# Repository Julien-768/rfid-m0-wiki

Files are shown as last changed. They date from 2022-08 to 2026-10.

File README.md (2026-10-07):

# RFID-M0 Documentation

Documentation for the **RFID-M0** autonomous monitoring device developed by the MIBE technical platform at IPHC.

This repository contains the source files used to build the RFID-M0 documentation website.

## Repository

The **GitLab repository is the primary project repository**. The GitHub repository is maintained as a mirror.

- **GitLab:** <https://gitlab.in2p3.fr/rfid-m0/rfid.m0.wiki>
- **GitHub:** <https://github.com/Julien-768/rfid-m0-wiki>

## Documentation website

The latest version of the documentation is available online:

**<https://rfid-m0.pages.in2p3.fr/rfid.m0.wiki/latest/>**

## Contents

The documentation covers the complete RFID-M0 project, including:

- device operation;
- user procedures;
- configuration;
- hardware architecture;
- electronic boards;
- power supply;
- RFID antennas;
- assembly;
- programming;
- manufacturing;
- testing and maintenance;
- advanced technical topics.

The documentation is available in **English and French**.

## Repository structure

```text
rfid.m0.wiki/
├── docs/               # Documentation source files
├── overrides/          # MkDocs theme customizations
├── mkdocs.yml          # MkDocs configuration
├── requirements.txt    # Python dependencies
├── pyproject.toml      # Project/tool configuration
├── .markdownlint.json  # Markdown linting configuration
└── .prettierrc         # Prettier configuration
```

## Requirements

The documentation is built using **MkDocs** with the **Material for MkDocs** theme.

Install the required Python packages with:

```bash
pip install -r requirements.txt
```

## Local development

To preview the documentation locally:

```bash
mkdocs serve
```

The development server is then available at:

```text
http://127.0.0.1:8000/
```

To build the static website:

```bash
mkdocs build
```

The generated website is placed in the `site/` directory.

## Firmware

The RFID-M0 firmware is maintained in a separate repository.

- **GitLab:** <https://gitlab.in2p3.fr/rfid-m0/rfid.m0.code>
- **GitHub:** <https://github.com/Julien-768/rfid-m0-code>

Firmware changes that affect device operation or documented behaviour should be reflected in this repository.

## Contributing

Documentation improvements, corrections, and clarifications are welcome.

When modifying documentation, please keep the structure and terminology consistent with the existing project documentation.

## License

This documentation is distributed under the **GNU General Public License v3.0**.

See [`LICENSE.txt`](LICENSE.txt) for the complete license text.

## Project

**RFID-M0**
MIBE Technical Platform — IPHC

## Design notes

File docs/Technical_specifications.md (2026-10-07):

# Technical specifications

## Memory

The system stores its data on a Micro-SD card.

- The maximal supported size is 32GB ([SD and SDHC](https://www.arduino.cc/reference/en/libraries/sd/) card supported).
- For example, a 2GB SD card can record ~5,100,000,000 detections with tags (**~59 continuous days** with one detection per second).

## Powering

Several powering options are proposed :

- Lithium powered
  - 3.6V 20Ah 72Wh Li-ion battery (Weight ~0.3kg - Cost ~80€ )
  - 3.6V 20Ah 72Wh Li-ion battery (Weight ~0.3kg - Cost ~80€ ) + a solar panel

- Lead powered
  - 12V 5.4Ah 64.8Wh Lead battery (Weight ~1.7kg - Cost ~40€ ), for rodent device

## Consumption & Autonomy

For details about components consumption and autonomy calculation, refers to the [calculation sheet](./assets/images/User_description/Consumption_and_autonomy.xlsx).

### Autonomy

The autonomy varies according to the software configuration. Here is the autonomy measured with a 65 Wh battery

| System configuration                |  Autonomy  | Equivalent consumption [W.h] | Equivalent consumption per day |
| ----------------------------------- | :--------: | :--------------------------: | :----------------------------: |
| IR On - RFID (On) (1) - 12/24h mode | 17d 7h 9m  |           0.16 W.h           |            3.8 /day            |
| IR On - RFID (On) (1) - 24/24h mode | 10d 22h 9m |           0.25 W.h           |            6 W/day             |
| IR Off - RFID On - 12/24h mode      | 9d 8h 37m  |           0.29 W.h           |            7 W/day             |
| IR Off - RFID On - 24/24h mode      | 5d 6h 34m  |           0.52 W.h           |           12.5 W/day           |

??? note "RFID (On)"

      RFID triggered by infrared sensors

??? note Assomptions made for autonomy estimation

    - 50 detections with RFID tag per hour
    - One detection = 5 seconds in front of sensor, including 1 second to read the RFID tag
    - a 64.8Wh 12V 5.4 A.h Lead battery (more pessimistic situation)
    - T = 20°c

Some notions have to be kept in mind :

- There is no consumption difference if one or two IR sensors are active. In both cases, the two emitters & receivers are powered
- If the two IR sensors are inactive, the RFID is always in research mode (IR Off - RFID On) except during sleep mode
- If the temperature sensor is active, the IR receiver modules are powered even if opt_IR_1 & opt_IR_2 are False (same power supply)
- During sleep mode, only the microcontroler and the Real Time Clock are powered

### Component consumption

| Board           | Component                    |   Mode   | Power consumption [mW] |
| --------------- | ---------------------------- | :------: | :--------------------: |
| Power board 5V  | Power board                  |    -     |           43           |
| Power board 12V | Power board                  |    -     |          112           |
| Main board      | Feather (including SD) + RTC |    -     |           65           |
| Main board      | RFID reader & antenna        | Standby  |           80           |
| Main board      | RFID reader & antenna        | Research |          450           |
| Main board      | RFID reader & antenna        | Reading  |          232           |
| Main board      | 1 IR Emitting Diode          |    -     |          15.8          |
| Main board      | 1 IR receiver module         |    -     |          1.3           |
| Main board      | + 3.3V regulator             |    -     |           45           |

The consumptions are measured for T = 20°c.

The IR Emitting Diode is considered with 220 Ohm resistor and 50% PWM duty cycle.

**Be careful to the SD card consumption** : Its consumption can vary from 1 et 10mA according to the manufacturer and the production batch.

### Rodent device dimensions

The system is designed to be integrated into a [1150 hard case Pelicase](https://www.peli.com/eu/fr/product/cases/protector/1150) (240 x 198 x 109 mm).

<a href="../assets/images/User_description/1150_pelicase.jpg">
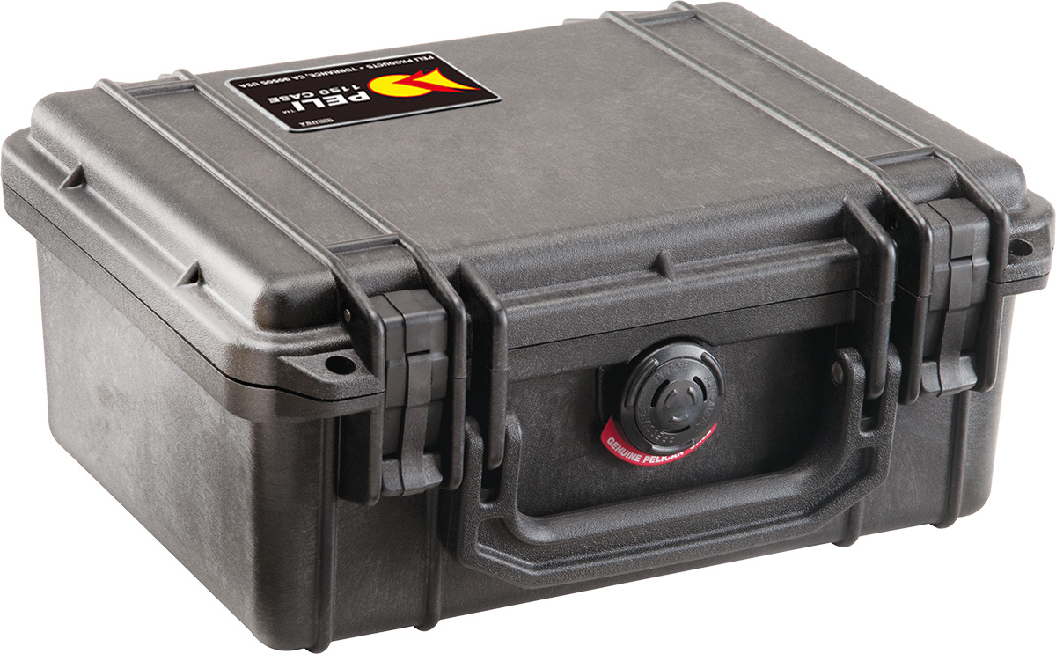
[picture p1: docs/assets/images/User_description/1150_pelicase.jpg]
1150 Pelicase

</a>

The operating tempererature range is 0°c to 50°c.

<!-- | System configuration                | Consumption [W.h] |  Autonomy  |
| ----------------------------------- | :---------------: | :--------: |
| I---------------------------------e | 3---------------7 | 1--------m |
| IR On - RFID (On) (1) - 24/24h mode | 5.9               | 10d 22h 9m |
| IR Off - RFID On - 12/24h mode      | 6.9               | 9d 8h 37m  |
| IR Off - RFID On - 24/24h mode      | 12.3              | 5d 6h 34m  | -->

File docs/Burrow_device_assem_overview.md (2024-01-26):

# Assembly a burrow device

This section describes the different steps to follow to assemble a device that monitor a burrow occupation. The list of required material is avaible at this [link](https://gitlab.in2p3.fr/rfid.m0/rfid.m0.elec/-/raw/master/BOM_append.xlsx?inline=false).

Firstly, a **burrow antenna is build**. This antenna receives the RFID antenna, able to detect RFID tags, but also two infrared sensors. The manufacturing of this device is based on 3D-printed parts in which electronic components are inserted. Resin is then added to protect the components from environment and rodents.

<a href="../assets/images/Antennas/burrow_antenna.jpg">
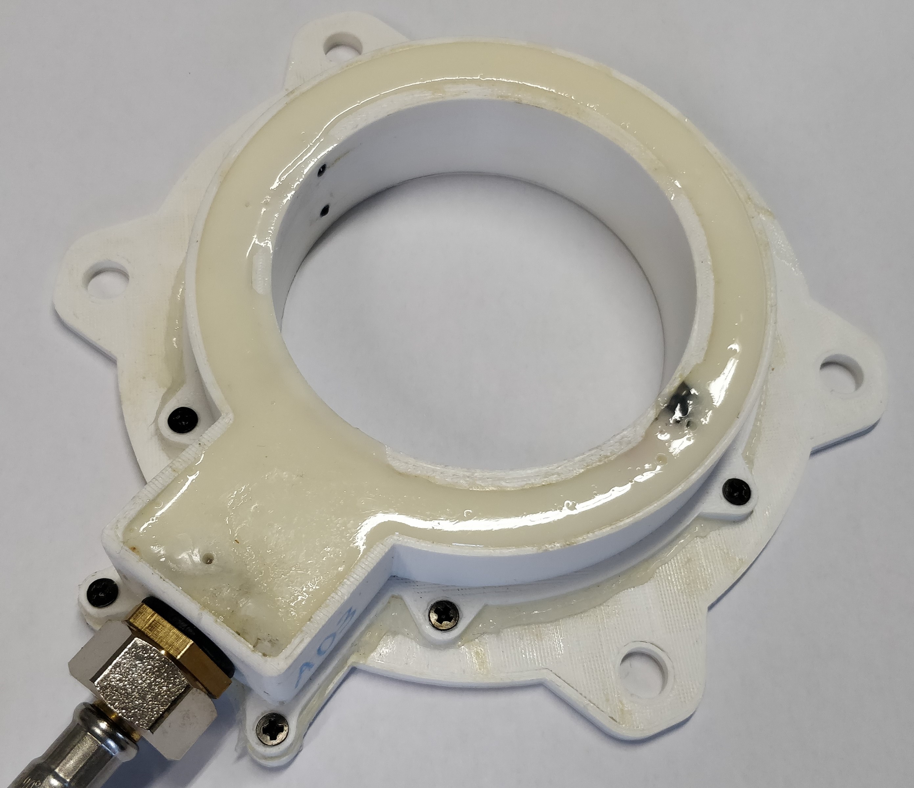
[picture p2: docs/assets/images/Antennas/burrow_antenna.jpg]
snapshot of the burrow antenna in the lab

</a>

Secondly **electronic component are mounted** into the boards. There are three boards that are required :

- A main board
- A power board in charge of power management
- A RFID reader based on a Tectus board

The last board only requires to weld some connectors. The power board (two variants exist) must be chosen according to the battery technology.

**A case is then prepared** and assembled with the antenna. The machining of the case must be carefully done to prevent water from entering the housing.

<a href="../assets/images/Case/Case_with_components.jpg">
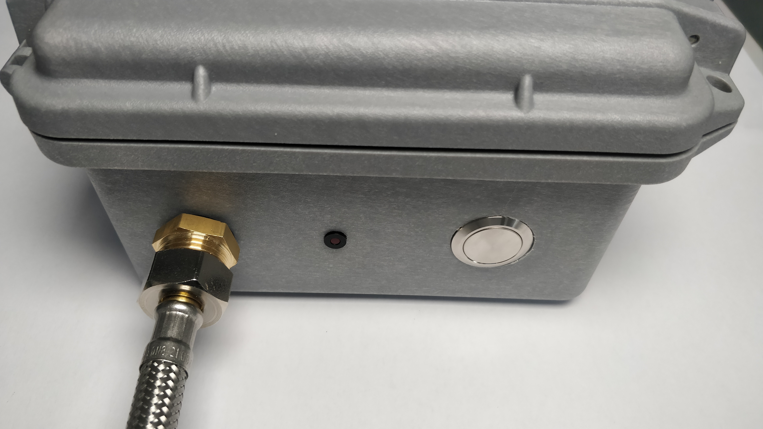
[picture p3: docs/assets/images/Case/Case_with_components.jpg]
Case with external components

</a>

The last step before the final assembling is to **program the main board**. This step must be done after the electronic assembling in order to correctly set the time of the real-time-clock (CR1220 coin cell must be inserted).

Finally **all the components are installed into the case**. This step requires wiring to connect the different boards together.

Once battery inserted and connected, the device will be ready for [checking](Check_burrow_device.md).

<a href="../assets/images/Burrow_assembling/Final_assembling.jpg">
Final assembling
</a>

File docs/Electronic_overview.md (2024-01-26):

# Overview

The electronic of the device is composed of several boards :

- A main board that receive most of the component and is linked to the sensors
- A power board in charge to manage the energy of the system and deliver a regulated 5v
- A RFID board that, once associated to an antenna, reads the RFID tags
- An optional multiplex board to connect two antennas to the main board

## Schematic of the system

<a href="../assets/images/Manufacturing/General_schematic.svg">
General schematic
</a>

For multiplexed version, [refer here](./assets/images/Manufacturing/General_schematic_multiplex.svg)

## Main board

The main board performs most of the system's functions :

- Sensor reading
- Data recording
- Time / Date management
- Security management (temperature and battery monitoring)

This board is **3.3V-logic level and powered in 5V** by one associated power board.

## Power board

The power board ensures the power and battery management to create a 5V.
Some components are plugged into it :

- The SWITCH button that **connect / disconnect the battery** to the power board
- The START button that permits the user to **safely switch On / Off** the system
- An optional solar panel to reload the battery

A 3-wire cable connect the main board to the power board :

- EN : This line permits the main board to pilot the power supply (self-hold function)
- SW : This line allow the main board to read the START button status (pressed / released)
- VBAT : Battery voltage compatible with 3.3V-logic level

To be compatible with different battery technologies, two power boards are available :

- [5V power supply board](./Power-5V.md) to use Li-Po or Li-Ion battery. A reload by USB-C or an optional solar panel is also possible.
- [12V power supply board](./Power-12V.md) to use lead-battery from 9V to 18V.

## Multiplex board

The multiplex board ensures to connect two antennas to the main board by routing :

- RFID signal
- Infrared signal
- Power signal

This board is **powered in 5V** and is compatible with **3.3V or 5V-logic level**.

Note : If a multiplex board is used, the servo motor cannot be connected (same pin)

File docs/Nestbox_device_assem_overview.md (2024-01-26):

# Assembly a nest box device

This section describes the different steps to follow to assemble a device that monitor a nest box occupation. The list of required material is avaible at this [BOM link](https://gitlab.in2p3.fr/rfid.m0/rfid.m0.elec/-/raw/master/BOM_append.xlsx?inline=false).

Firstly, a **nest box antenna is build**. This antenna receives the RFID antenna, able to detect RFID tags, but also two infrared sensors. The manufacturing of this device is based on 3D-printed parts in which electronic components are inserted and glued.

<a href="../assets/images/Antennas/schwegler_antenna.jpg">
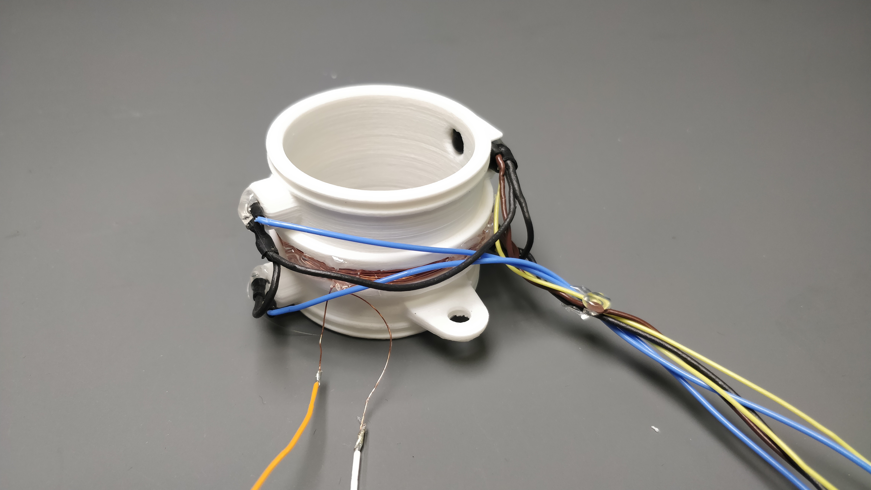
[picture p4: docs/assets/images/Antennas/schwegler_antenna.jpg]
wired antenna and infrared beams around the 3D print in the lab

</a>

Secondly **electronic component are mounted** into the boards. There are three boards that are required :

- A main board
- A power board in charge of power management
- A RFID reader based on a Tectus board

The RFID board only requires to weld some connectors.

Due to the dimensions of the nest box, **only the 5v power board can be used**. In addition, the compatibility with an additional solar panel or USB charger is possible.

The last step before the final assembling is to **program the main board**. This step must be done after the electronic assembling in order to correctly set the time of the real-time-clock (CR1220 coin cell must be inserted).

Finally **all the components are installed into the nest box and wired**. This step requires 3D-printing and wiring to connect the different boards together.

Once battery inserted and connected, the device will be ready.

<a href="../assets/images/Nest_box_assem/Nest_box_closed.jpg">
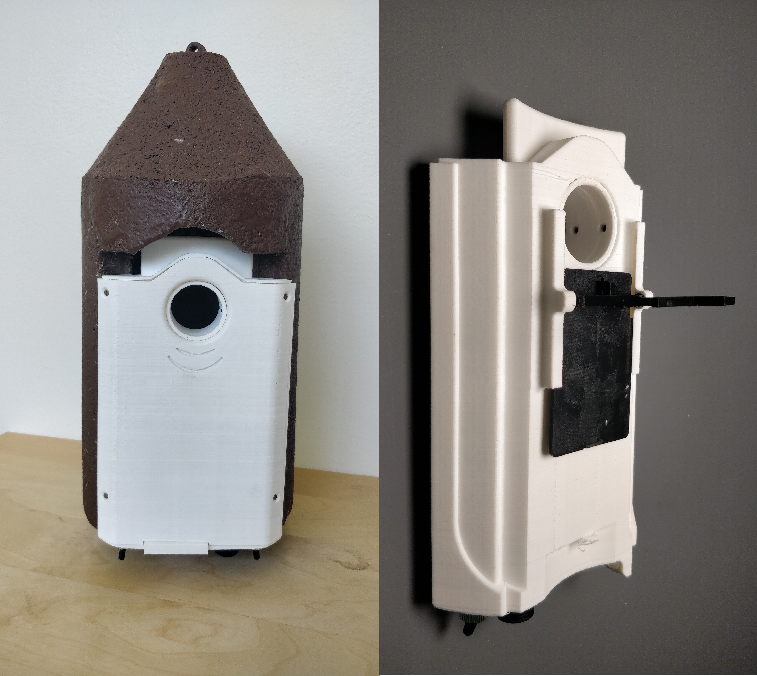
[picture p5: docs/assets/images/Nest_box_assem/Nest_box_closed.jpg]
Nest box assembled

</a>

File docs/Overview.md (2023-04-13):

# Overview

L'alimentation de la carte Acquisition est en 5V.

La "carte Power" assure la conversion et la gestion de la batterie, pour envoyer en sortie du 5V.

- L'interrupteur général coupe l'alimentation en entrée du convertisseur VBAT / 5V.
- Le bouton marche arrêt ou Switch, permet par un appui prolongé, l'allumage ou l'éteignage du système par le software.
- La recharge par panneau solaire est optionnel.

Les 3 câbles de données [EN;SW;Vbat] entre les 2 cartes servent à :

- EN: si cette entrée est mise à l'état haut, l'alimentation de l'acquisition est coupée.
- SW: passe à l'état haut si le bouton marche/arrêt est appuyé.
- Vbat: renvoie l'information de la tension de la batterie entre 0 et 3.3V à l'aide d'un pont diviseur

TODO Power_schematic_géné "/uploads/53b2525b21db5eaeaf2a90db03fd7f05/Power_schematic_géné.png"

Il a été conçu 2 types de carte Power:

- [5V power supply board](./Power-5V.md) qui permet d'utiliser des batteries Li-Po ou Li-Ion avec l'option rechargement par panneau solaire ou par USB C.
- [12V power supply board](./Power-12V.md) qui permet d'utiliser des batteries allant de 9V à 18V.

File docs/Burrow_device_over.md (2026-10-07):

# Device description

The purpose of this system is to monitor certain individuals.
A circular antenna, equipped with sensors and placed at the entrance of a burrow, can detect the passage of individuals and read their RFID tags (if existing).
All this data is collected on an memory card with timestamp.

The entire system is contained in a case for easy transport and installation.

<a href="../assets/images/User_description/Complete_system.jpg">
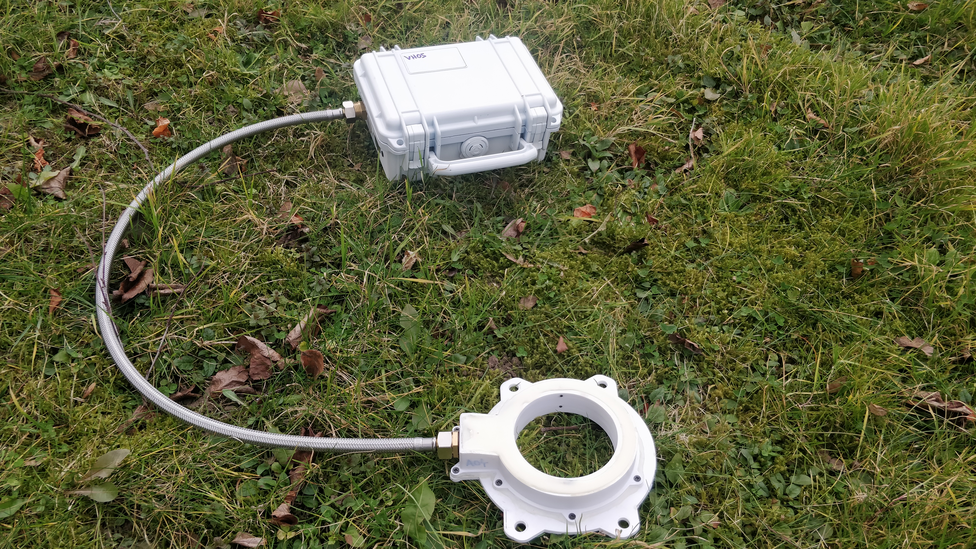
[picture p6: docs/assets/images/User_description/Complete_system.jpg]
Complete system

</a>
<<<<<<< Updated upstream

## System constitution

=======

> > > > > > > Stashed changes

The system consists of a terrier antenna and a case.
The antenna incorporates two infrared transmitters / receivers as well as an RFID antenna.

<a href="../assets/images/User_description/Burrow_device_detailed.jpg">
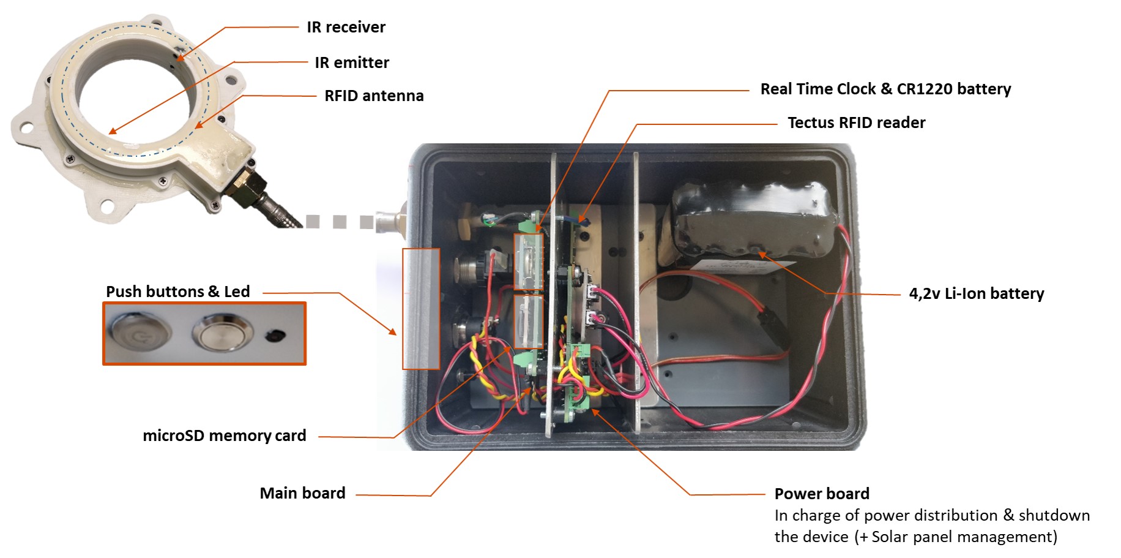
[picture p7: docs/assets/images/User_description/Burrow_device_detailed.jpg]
Burrow device detailed

</a>

Note : IR sensor noted "IR 1" in the record file is the one mounted on the top of the antenna (small diameter side)

<a href="../assets/images/User_description/IR_sensor_arrangement.png">
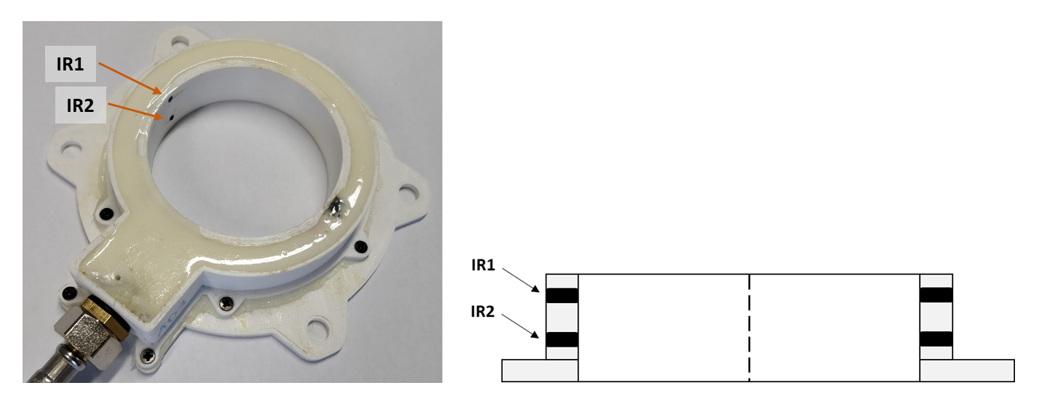
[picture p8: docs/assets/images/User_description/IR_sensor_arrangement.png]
IR sensors arrangement

</a>

The case contains all the embedded electronics, the battery, the clock, the micro-SD memory card and the start-up buttons.
On the outside of the case you'll find:

- A main switch button : Used to connect / disconnect the system with the battery
- A switch button : Used to power-on / power-off the system / get the battery status
- A red LED : Used by the system to interact with the user

<a href="../assets/images/Procedure/External_component.png">
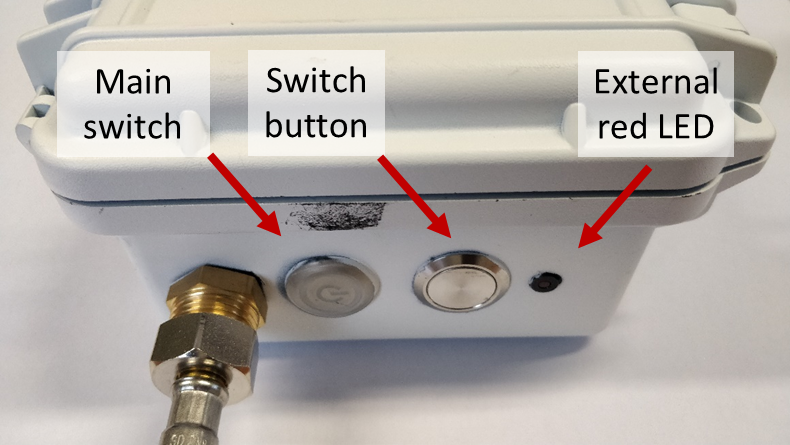
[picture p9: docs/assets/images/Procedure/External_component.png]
External component

</a>

Inside the case is:

- A battery (4.2V Li-ion or 12V Lead version)
- A slot for the micro-SD memory card
- A CR1220 3V battery for the Real-Time Clock

<a href="../assets/images/User_description/Internal_component.png">
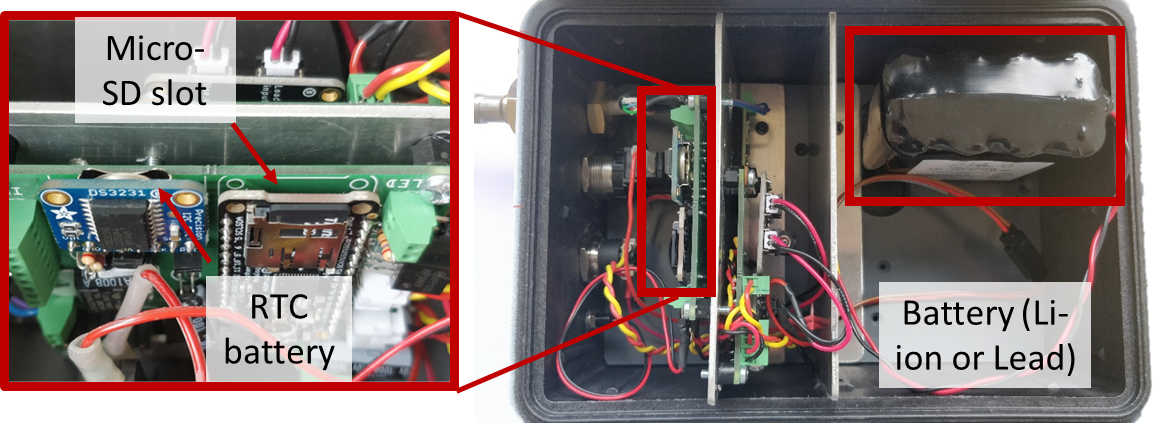
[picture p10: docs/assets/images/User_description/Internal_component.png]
Internal component

</a>

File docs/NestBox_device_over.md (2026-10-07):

# Device description

The purpose of this system is to monitor certain birds. The entrance of a nest box is equipped with sensors to detect the passage of individuals and read their RFID tags (if existing). All this data is collected on a memory card with a timestamp.

Optionally, the nest box door can be closed to capture targeted individuals: None, All, specific RFID tag, or untagged.

The entire system is contained in a door compatible with [Schwegler nest box 2M](https://www.schwegler-natur.de/portfolio_1408366639/nisthoehle-2m/?lang=en).

<a href="../assets/images/User_description/Nest_box_installed.jpg">
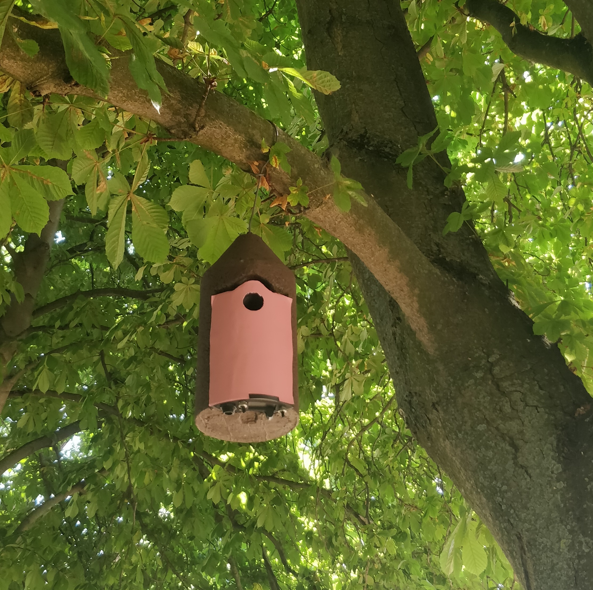
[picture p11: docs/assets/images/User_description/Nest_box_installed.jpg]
Nest box installed

</a>

## Mechanical specifications

### Dimensions

The manufactured door is approximately 210 mm high, 122 mm wide, and 34 mm deep.

### 3D preview

<iframe id="vs_iframe" src="https://www.viewstl.com/?embedded&url=https%3A%2F%2Fgitlab.in2p3.fr%2Frfid.m0%2Frfid.m0.meca%2F-%2Fraw%2Fmaster%2Fantenna_schwegler%2F3D_print%2FFake_device%2FAssembly.stl%3Finline%3Dfalse&orientation=bottom&shading=flat&bgcolor=transparent" style="border:0;margin:0;width:100%;height:601px;"></iframe>

## System Components and Features

### 1 - Entrance Components

The entrance of the nest box incorporates two infrared transmitters/receivers as well as an RFID antenna.

**Note:** The IR sensor noted as "IR 1" in the record file is the one mounted at the entrance (exterior side).

### 2 - Bottom Components

The bottom of the nest box allows the user to interact with the system and its battery:

- A main switch button: Used to connect/disconnect the system from the battery.
- A switch button: Used to power on/power off the system or get the battery status.
- A red LED: Used by the system to interact with the user.
- A mini-USB port: Used to recharge the internal battery or connect an additional battery to extend autonomy (power bank, solar panel, etc.).
- A ring: Used to hold a power bank via a carabiner.

<a href="../assets/images/User_description/Nest_box_Ext_comp.jpg">
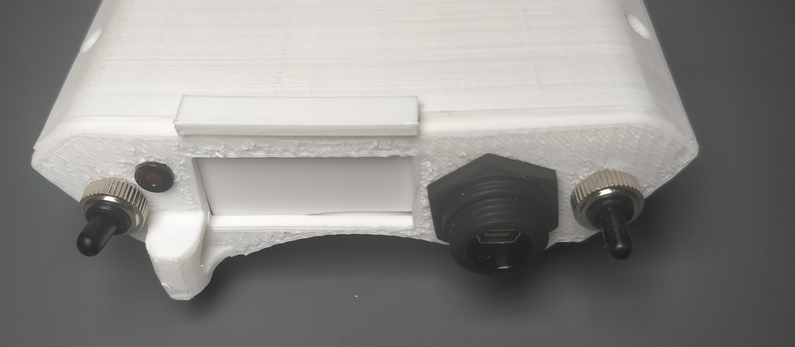
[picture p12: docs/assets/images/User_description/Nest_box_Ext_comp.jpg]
Nest box external component

</a>

### 3 - Technical Door

By sliding the technical door, it is possible to access:

- A slot for the micro-SD memory card.
- A CR1220 3V battery for the Real-Time Clock.

<a href="../assets/images/User_description/Nest_box_Int_comp.jpg">
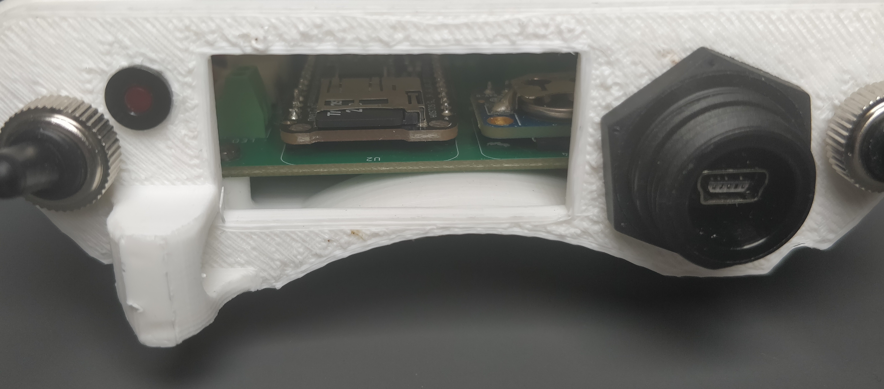
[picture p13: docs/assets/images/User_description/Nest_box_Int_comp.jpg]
Nest box internal component

</a>

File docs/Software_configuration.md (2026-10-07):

# Software configuration

The device configuration is split into two files:

- `hw_assem.cfg`: hardware and device identification parameters.
- `config.cfg`: functional and operating parameters.

These files allow the device to be adapted to the specific hardware and application requirements.

## Hardware configuration — `hw_assem.cfg`

The `hw_assem.cfg` file contains hardware identification and device specification parameters.

| Parameter name      | Description                                                                             | Default / example     |
| ------------------- | --------------------------------------------------------------------------------------- | --------------------- |
| `uid_mainboard`     | Unique identifier of the mainboard (FeatherM0), automatically retrieved by the software | Device-specific       |
| `uid_light_sensor1` | Unique identifier of light sensor 1, automatically retrieved by the software            | Installation-specific |
| `uid_light_sensor2` | Unique identifier of light sensor 2, automatically retrieved by the software            | Installation-specific |
| `uid_software`      | Unique software identifier used to identify the specific firmware version installed     | Installation-specific |
| `uid_experiment`    | Unique identifier of the experiment or project                                          | Installation-specific |
| `device_sn`         | Device serial number used to uniquely identify the physical unit                        | Empty                 |
| `battery_type`      | Type of battery used by the device                                                      | `liion_1s`            |
| `rtc_type`          | Real-Time Clock module used by the device                                               | `ds3231`              |

The `uid_light_sensor1`, `uid_light_sensor2`, `uid_software`, `uid_experiment` and `device_sn` parameters are specific to each installation and should be configured according to the deployed device.

## Functional configuration — `config.cfg`

The `config.cfg` file contains the parameters controlling the functional behavior of the device.

| Parameter name           | Description                                                                               | Values / default          |
| ------------------------ | ----------------------------------------------------------------------------------------- | ------------------------- |
| `use_buffer`             | Enables or disables the use of a temporary data buffer before writing data to the SD card | `{true, false}` — `false` |
| `enable_ir1`             | Enables or disables infrared sensor 1                                                     | `{true, false}` — `true`  |
| `enable_ir2`             | Enables or disables infrared sensor 2                                                     | `{true, false}` — `true`  |
| `enable_rfid`            | Enables or disables the RFID reader                                                       | `{true, false}` — `true`  |
| `rfid_mode`              | Defines how and when the RFID reader is activated                                         | `{0, 1, 2}` — `1`         |
| `enable_vbat`            | Enables or disables battery voltage measurement                                           | `{true, false}` — `true`  |
| `acquisition_interval_s` | Interval between two consecutive data acquisitions, in seconds                            | `[1..xx]` — `60`          |
| `schedule_start_hour`    | Operating schedule start hour                                                             | `[0..23]` — `10`          |
| `schedule_start_minute`  | Operating schedule start minute                                                           | `[0..59]` — `00`          |
| `schedule_end_hour`      | Operating schedule end hour                                                               | `[0..23]` — `18`          |
| `schedule_end_minute`    | Operating schedule end minute                                                             | `[0..59]` — `30`          |

The `schedule_start_*` and `schedule_end_*` parameters define the automatic operating period of the device. With the default values shown above, the operating period is **10:00 to 18:30**.

## RFID mode

The `rfid_mode` parameter defines how and when the RFID reader is activated.

| Value | Mode        | Behavior                                                                                                                                                                                                           | Power consumption |
| ----: | ----------- | ------------------------------------------------------------------------------------------------------------------------------------------------------------------------------------------------------------------ | ----------------- |
|   `0` | Disabled    | The RFID reader is switched off. No tag detection is performed.                                                                                                                                                    | Very low          |
|   `1` | Continuous  | The RFID reader remains continuously active and detects tags continuously.                                                                                                                                         | High              |
|   `2` | On IR event | The RFID reader is activated temporarily following a detection by an infrared sensor.This mode is suitable for relatively large or slow-moving animals that take sufficient time to pass through the RFID antenna. | Moderate          |

### Mode 0 — Disabled

The RFID reader is switched off and no RFID tag detection is performed.

This mode can be used when RFID functionality is not required.

### Mode 1 — Continuous

The RFID reader remains continuously active and can detect tags at any time.

This mode provides continuous RFID availability but results in higher power consumption.

### Mode 2 — On IR event

The RFID reader is activated temporarily following an event detected by an infrared sensor.

This mode reduces power consumption by activating the RFID reader only when an IR event occurs.

**Note:** Mode `2` requires at least one infrared sensor to be enabled (`enable_ir1` or `enable_ir2`).

## RFID activation timing

In mode `2`, the RFID reader is activated for a limited period following an IR event.

The default activation period is between **2 and 5 seconds**. A **1-second debounce period** is used to avoid repeated detections of the same tag.

These timings are predefined and do not need to be modified through the configuration file.

## Editing the configuration files

To modify a configuration file:

1. Remove the SD card from the device and insert it into a computer.
2. Locate the required configuration file (`hw_assem.cfg` or `config.cfg`).
3. Open the file with a text editor.
4. Modify the required parameters.
5. Save the file and reinsert the SD card into the device.

_NOTE:_ Take care to preserve the file syntax when modifying configuration parameters. Incorrect formatting or invalid values may prevent the device from loading the configuration correctly.

If a required configuration file is not present on the SD card, the device can automatically create it with its default values.

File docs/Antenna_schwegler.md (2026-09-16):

# Antenna for Schwegler

This antenna is designed for use on 3D printed door for [Schwegler nest box 2M](https://www.schwegler-natur.de/portfolio_1408366639/nisthoehle-2m/?lang=en), it is suitable with the Tectus RFID reader TITAN 4004 (also know as TLB-30-USB).

<a href="../assets/images/Antennas/schwegler_antenna.jpg">
<<<<<<< Updated upstream
wired antenna and infrared beams around the 3D print in the lab
=======
wired antenna and infrared beams around the 3D print in the lab
>>>>>>> Stashed changes
</a>

## Radiating pattern

The radiation pattern was measured with a 2.3mm EM4102 PIT Bird Tag from [Eccel Technology Ltd.](https://eccel.co.uk/product/2-3mm-em4102-pit-bird-tag-black/)
The read range is 400 mm (typical values) with a EM4102 transponders (1.7 mm Ø) in the best conditions.
The following results are measured on an antenna with a quality factor Q = 23.

<a href="../assets/images/Antennas/schwegler_radiation_best.png">
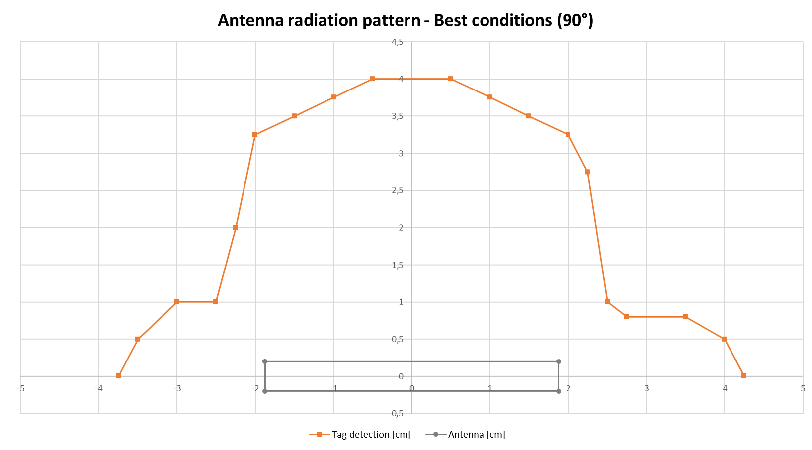
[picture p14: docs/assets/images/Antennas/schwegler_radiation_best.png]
image of the radiation pattern of the Schwegler antenna with best TAG orientation

</a>
<a href="../assets/images/Antennas/schwegler_radiation_worst.png">
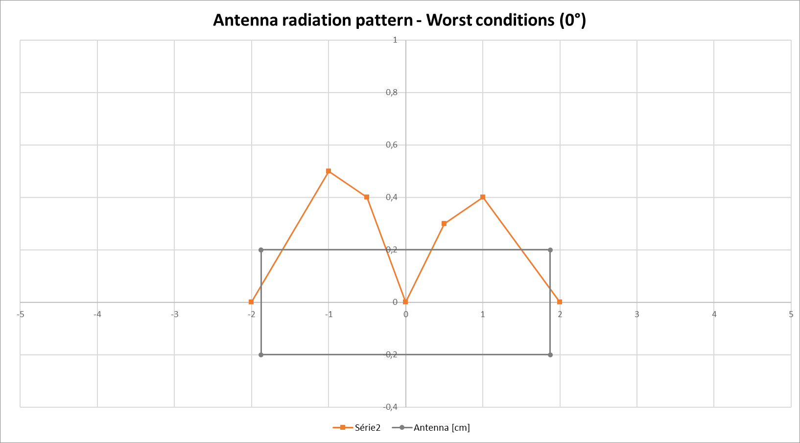
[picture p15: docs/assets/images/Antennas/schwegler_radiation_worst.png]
image of the radiation pattern of the Schwegler antenna with worth TAG orientation

</a>

## Mechanical specifications

### Dimensions

The internal diameter a the mechanical part is 32 mm. It is designed for great tits bird species. The depth the bird would have to cross is 34 mm.
The wired antenna itself is an circle of Ø36 mm by TODO height . You can access the [mechanical schematic on the repository](https://gitlab.in2p3.fr/rfid.m0/rfid.m0.meca/-/tree/master/antenna_schwegler)

### 3D preview

<iframe id="vs_iframe" src="https://www.viewstl.com/?embedded&url=https://gitlab.in2p3.fr/rfid.m0/rfid.m0.meca/-/raw/master/antenna_schwegler/Antenna.stl?inline=false" style="border:0;margin:0;width:100%;height:400px;"></iframe>

## Electronic specifications

The antenna inductance is around 192µH to be compliant to the Tectus RFID reader TITAN 4004. It is suitable with the 125 - 134 kHz frequency range. It requires 7.5 m of Ø0.2mm enamelled copper wire which would make ~67 spires.

## Assembling instructions

Please refer to the [Developper section of the project for assembling instructions](./Assembling_antenna.md).

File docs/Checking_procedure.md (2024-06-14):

# Checking procedure

This page describes a simple procedure to check your hardware, either on the field or in your office.

## Before testing

1. Plug-in the battery
2. Check the SD memory card and the RTC battery are in their slots

<a href="../assets/images/Procedure/Battery_connection.png">
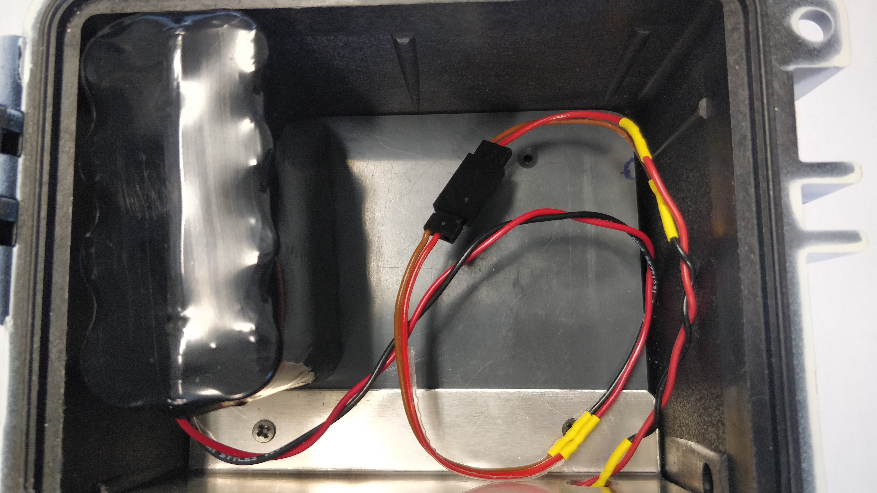
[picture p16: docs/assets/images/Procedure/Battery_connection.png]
battery connection

</a>
<a href="../assets/images/Procedure/External_component.png">
external component illustration
</a>

---

## Test procedure

### SD card and Real-Time Clock

We are going to check the SD card and the RTC are in order by checking the LEDs of the device.

1. Press the main switch (with power symbol, pressed = On)
2. Press the switch button until the red LED turns on. Once done, release it. The red LED should turn OFF after the startup of the device.
   - If the red LED does not light up at all, check that the battery connector is well plugged-in
   - If the red LED is blinking 2 times, the memory card is not found or is faulty, reinsert it or replace it.
   - If the red LED is blinking 4 times, the CR1220 coil cell battery might be faulty, replace it. Then the main board must be [reprogrammed](./programming.md)

### Infrared beam

_Please note_ as the angle of the IR cells is wide, it is important to properly cover the infrared receiver.

We are going to check if the infrared beams are working by checking the RFID reader's LED. The RFID reader only tries to read tags after an infrared event is detected, and this causes its LED to blink.

1. Once the device is started and the red LED is off, set your finger on one of the infrared receivers. Check that the RFID reader light turns on for a few seconds (flashing red light)
2. After a few seconds, remove your finger and check that the RFID reader light stays on for a few seconds (flashing red light)
3. Repeat the same operation with the second infrared receiver

It is possible to differentiate the bigger diameter of the IR receiver module from the emitter. In addition, The receiver is mounted on the right side of the antenna.

<a href="../assets/images/Procedure/RFID_led.png">
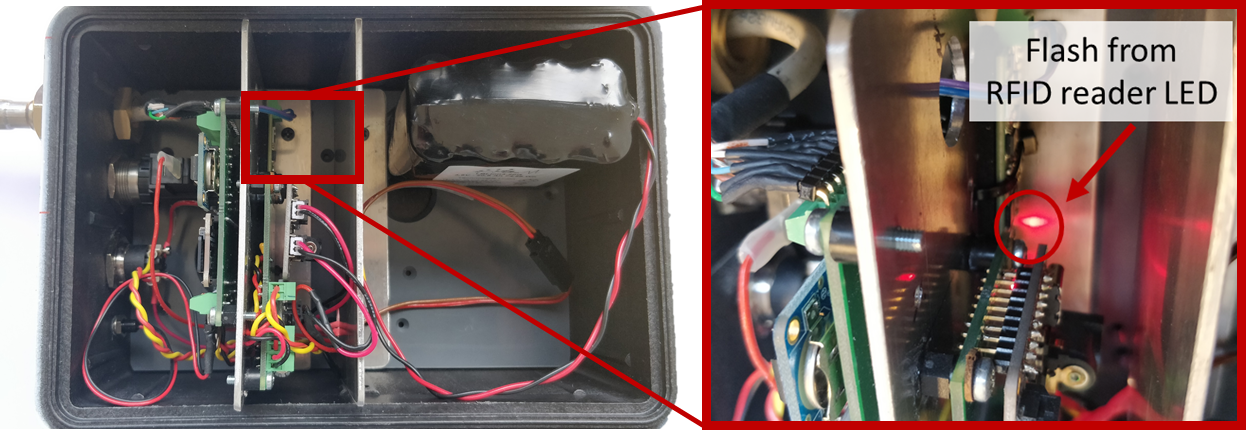
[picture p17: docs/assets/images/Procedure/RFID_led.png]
RFID led

</a>
<a href="../assets/images/Procedure/IR_receiver.png">
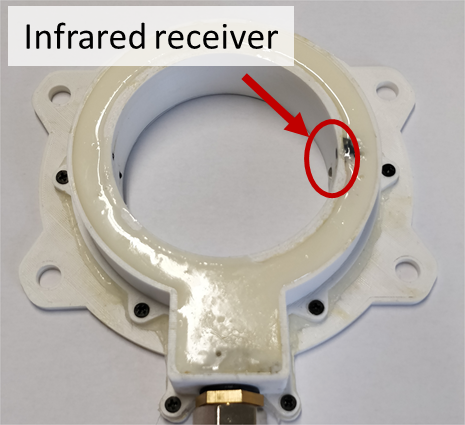
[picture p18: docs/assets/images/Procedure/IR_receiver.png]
IR receiver module

</a>

### RFID reader

_Please note_ this test must be performed within 5 minutes after the system power-on. After this delay, the red LED will be disabled for energy saving reasons.

We are going to check if the RFID reader is able to detect and read a RFID tag, by passing one into the antenna and checking the red LED.

1. Pass your hand with a tag through the antenna
2. Check that the red LED flashes briefly

### Device shutdown

1. Maintain the switch button pressed until the red LED stops blinking and remains on
2. Release the switch button
3. Press main switch (released = Off)
4. Disconnect the battery

### SD card content and date / time

_Please note_ the time base is expressed in UTC time period

We are going to check if the SD card is correctly working (write data) and if the real-time clock is up-to-date by checking the content of the saved files.

1. Once the previous tests are done, turn off the device and insert the SD card into a computer
2. Check for a text file nammed with the current date (date format : YY_MM_DD.TXT). If it is the case, open it
3. In the file, check that the different events of the tests are present and that the associated time is correct
   - If the time is not correct
     - [Reprogram](./programming.md) the micro-controller to set up the time
     - check the RTC battery

??? "File content"

    ```
    2023-5-4;13:4:3.123;MB202303001;inv_mainboard;uid_experiment;202303YH001;
    2023-5-4;13:4:3.123;MB202303001;inv_mainboard;System;Start;
    2023-5-4;13:4:10.123;MB202303001;inv_mainboard;System;RTC is ok;
    2023-5-4;13:4:28.301;2303002591056;inv_rfid_sensor;IR 2;broken beam;
    2023-5-4;13:4:31.870;2303002591056;inv_rfid_sensor;IR 2;beam restored;
    2023-5-4;13:4:33.871;2303002591056;inv_rfid_sensor;IR 1;broken beam;
    2023-5-4;13:4:35.263;2303002591056;inv_rfid_sensor;IR 1;beam restored;
    2023-5-4;13:4:38.71;2303002591056;inv_rfid_sensor;IR 2;broken beam;
    2023-5-4;13:4:38.94;2303002591056;inv_rfid_sensor;IR 1;broken beam;
    2023-5-4;13:4:38.586;2303002591056;inv_rfid_sensor;A0;972-270000015773;
    2023-5-4;13:4:41.198;2303002591056;inv_rfid_sensor;IR 1;beam restored;
    2023-5-4;13:4:41.308;2303002591056;inv_rfid_sensor;IR 2;beam restored;
    2023-5-4;13:4:44.267;MB202303001;inv_mainboard;Vbat;Battery check by user;
    2023-5-4;13:4:44.267;MB202303001;inv_mainboard;Vbat;3.62V;
    2023-5-4;13:4:50.871;MB202303001;inv_mainboard;System;Shutdown : User;
    ```

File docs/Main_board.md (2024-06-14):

# Main board

This page describes the main board, that regroups the main sensors / components of the device.

## Schematic of the system

<a href="../assets/images/Manufacturing/Main_board_schema.svg">
Man board schematic
</a>

The main board has different voltage levels :

- 5V : Provided by the PW connector, the 5V is distributed to the Feather M0, the RFID module, the servomotor and the 3.3V voltage regulator
- 3V (permanent) : Provided by the internal Feather M0 regulator, this 3V powers the RTC module
- 3V (controlled) : Provided by the 3.3V regulator, this voltage powers the IR Emitting Diode & receiver and the temperature sensor (RTD)

As the Feather is a 3V3-logic level, all the inputs / outputs are **3V3-logic based**.

Several **communication modes** are used :

- [I2C](https://en.wikipedia.org/wiki/I%C2%B2C) for the RTC module
- [SPI](https://en.wikipedia.org/wiki/Serial_Peripheral_Interface) for the integrated SD card and the RTD module
- [UART](https://en.wikipedia.org/wiki/Universal_asynchronous_receiver-transmitter) for the RFID reader

For **power supply**, refers to the [Overview](./Electronic_overview.md) section.

## Materials

### Development board

<a href="../assets/images/Main_board/Feather_M0.png">
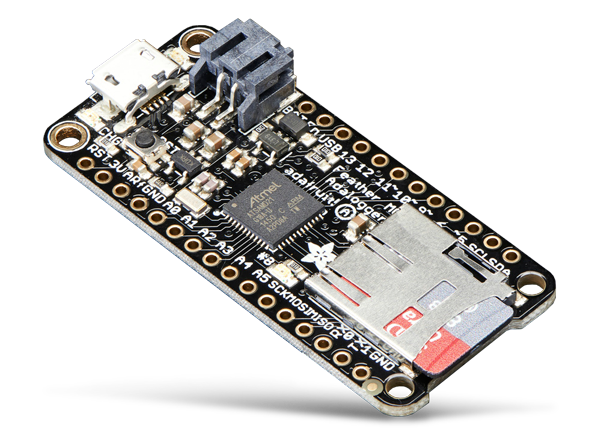
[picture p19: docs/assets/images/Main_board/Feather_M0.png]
snapshot of the Feather M0 board

</a>

The Adafruit Feather M0 Adalogger is an Arduino-type development board specially designed for data recording applications. Its 256 kB of flash allows to have a larger memory than most equivalent models. The recorded data are stored into the integrated microSD slot.
**This is a 3.3v-logic level board : Be careful to ensure the voltage compatibility when it's used with 5v-logic sensors**

More information about the board in the [Adafruit tutorial](https://learn.adafruit.com/adafruit-feather-m0-adalogger/overview)

Description of the pinout used :

<a href="../assets/images/Main_board/Feather_M0_pinout.png">
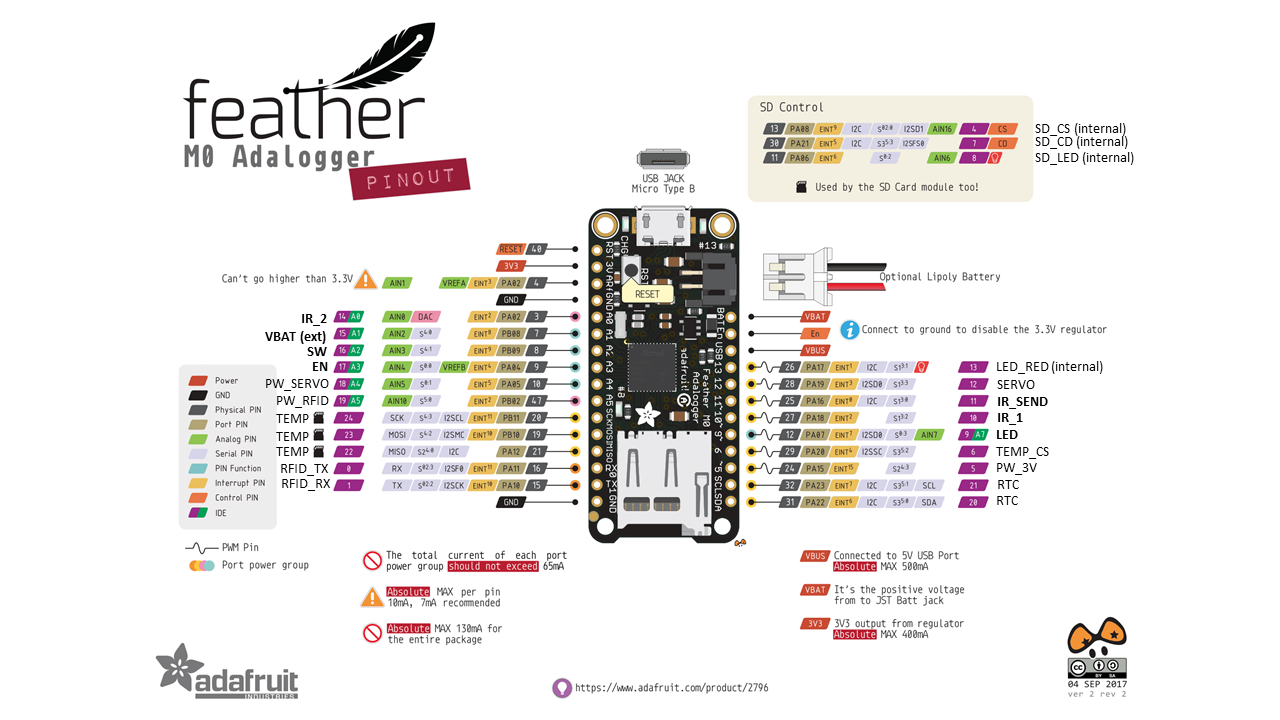
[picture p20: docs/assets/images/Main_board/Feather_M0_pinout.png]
Pin out with annotations of the Feather M0

</a>

### Servomotor

<a href="../assets/images/Main_board/ServoMotor.png">
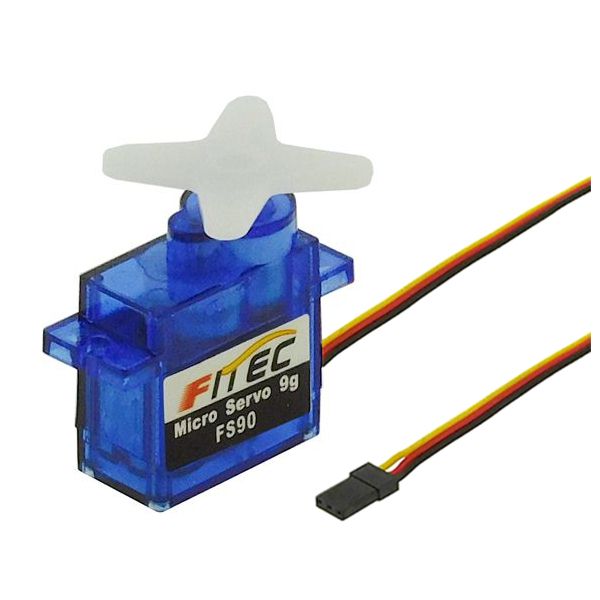
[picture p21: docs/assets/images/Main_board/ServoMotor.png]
snapshot of the servo-motor

</a>

The Feetech FS90 servomotor is suitable for miniaturized or energy-saving systems. With a rotational speed of 1.4 rev/s, it can deliver a maximal torque of 1.3 kg.cm.
5V power supply

For more details refers to the [datasheet](https://www.gotronic.fr/pj2-fs90-2549.pdf)

### Real-Time-Clock (RTC) module

<a href="../assets/images/Main_board/RTC_module.png">
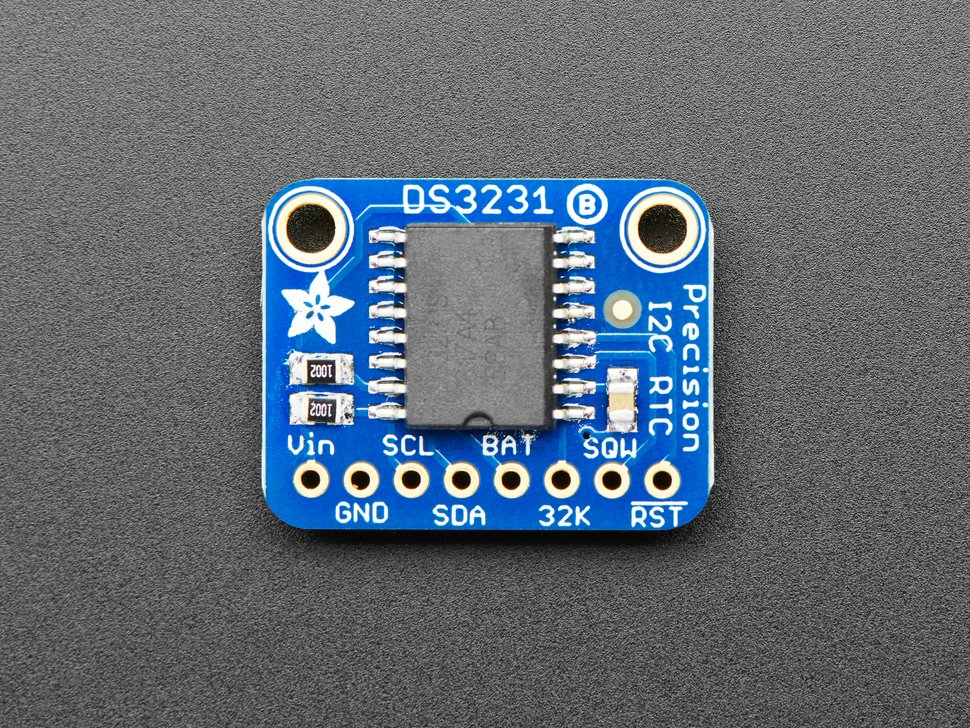
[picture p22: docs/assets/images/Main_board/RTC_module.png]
snapshot of the RTC module

</a>

This sensor keeps the date & time thanks to its internal battery and a very low power consumption (~110µA @ 3.6V in standby mode). This module communicates with an I2C link and can be resynchronized by software. Supply voltage from 2.3V to 5.5V
The internal battery is based on a [CR1220 3V lithium coin cell battery](https://www.adafruit.com/product/380)

More information about the board in the [Adafruit tutorial](https://learn.adafruit.com/adafruit-ds3231-precision-rtc-breakout/overview) and the [product specifications](https://www.adafruit.com/product/3013)

### RFID module

<a href="../assets/images/RFID/RFID_module.png">
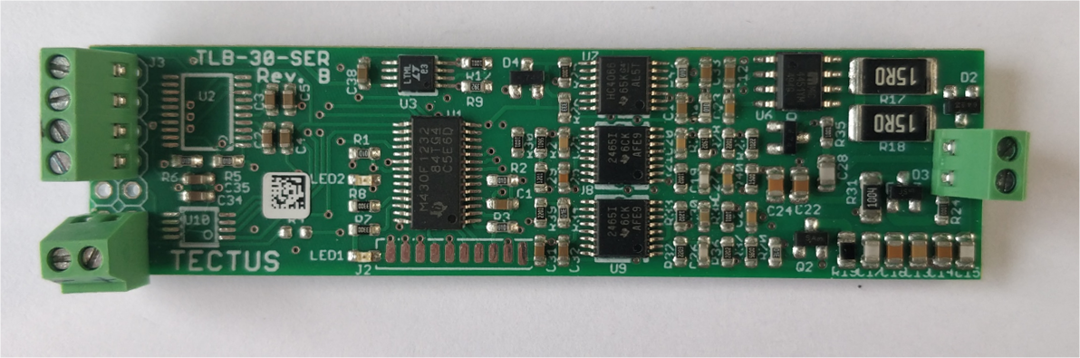
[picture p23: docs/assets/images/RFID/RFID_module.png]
snapshot of the RFID module

</a>

The Tectus RFID board supports the HDX, FDX and EM4102 protocols. Linked to a 190µH external antenna, its range mainly depends of the antenna size and the type of transponder used.

More information about the [connection pinout](./assets/images/Tech_doc/Connection_Drawing_TLB-30-SER.pdf) and the [communication](./assets/images/Tech_doc/scotty.v1.4_TLB-30-Commands_.pdf)

### Resistance-Temperature-Detector (RTD) sensor

<a href="../assets/images/Main_board/RTD_module.png">
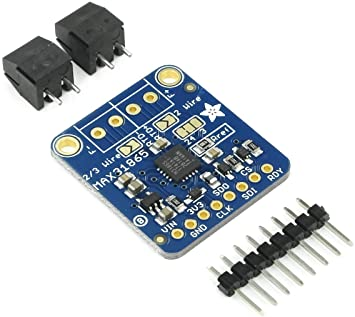
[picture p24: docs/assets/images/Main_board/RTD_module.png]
snapshot of the Resistance Temperature Detector sensor

</a>

This sensor measures the ambiant temperature thanks to a resistor that varies according to the temperature. The temperature admissible range is -200°c to +450°c. Supply voltage from 3V to 5V
To use this sensor with two-wires probe, solder the _2/3 wire_ et _2 wire_ plugs and ensure the wires are connected on the _F+_ et _F-_ terminals.

More information in the [Adafruit tutorial](https://learn.adafruit.com/adafruit-max31865-rtd-pt100-amplifier/overview)

### Infrared barrier

This 36kHz modulated infrared barrier filters out natural ambient infrared radiation, and frees itself from the brightness of the environment.

#### Infrared emitter

<a href="../assets/images/Main_board/IR_emitter.png">
snapshot of the infrared emitter
</a>

The TSAL4400 emitter is an infrared diode that emits a light of 940nm wavelength.
The cathode (-) is the shortest pin (no flat visible). Max admissible current : 100mA
To be compatible with the receiver, **this emitter has to emit a 36 kHz signal**. Refers to the [Infrared section](Infrared.md) to know how to create the modulation.

For more information refers to the [datasheet](https://www.vishay.com/docs/81006/tsal4400.pdf)

#### Infrared receiver

<a href="../assets/images/Main_board/IR_phototransistor.png">
snapshot of the Photo-receiver
</a>

The TSOP34536 infrared receiver is designed to work in very noisy environment and detects only a 36 kHz IR signal.
With a very low power consumption, it can be powered from 2.5V to 5.5V

For more information refers to the [datasheet](https://www.vishay.com/doc?82490)

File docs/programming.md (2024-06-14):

# Programming procedure

## Prerequisites

1. A main board assembled according to the [instructions](Electronic_assembling.md)
2. Download [Visual Studio Code](https://code.visualstudio.com/download)
3. Install [PlatfomIO](https://docs.platformio.org/en/stable/integration/ide/vscode.html#installation)
4. Clone the [rfid.m0.code](vscode://vscode.git/clone?url=https%3A%2F%2Fgitlab.in2p3.fr%2Frfid.m0%2Frfid.m0.code.git) repository
5. Get a [USB Micro B cable](https://en.wikipedia.org/wiki/USB_hardware#/media/File:MicroB_USB_Plug.jpg)
6. Set your computer in UTC time zone

## Programming

1. Open the code folder in Visual Studio Code. Give some time for the dependencies to be automatically downloaded once the code repository is cloned if it is a first time use.
2. Set hard defined options by commenting / uncommenting if necessary the line starting by

   ```c
   #define V2_0_0_PINOUT		// Comment to use pinout before v2.0.0 (before august 2023)
   #define LIION_BATTERY		// Comment to use lead battery
   #define RTC					// Comment to not use the RTC
   ```

3. Connect the Feather M0 to the computer using a USB cable
4. Click on [PlatformIO: Clean](https://docs.platformio.org/en/stable/integration/ide/vscode.html#platformio-toolbar) or Clean via the [PIO Menu](https://docs.platformio.org/en/stable/_images/platformio-ide-vscode-task-explorer-refresh.png). This will refresh the compilation date to update the RTC if needed.
5. Click on 'PlatformIO: Upload' and then open the 'PlatformIO: Serial Monitor' or 'Upload and Monitor' via the [PIO Menu](https://docs.platformio.org/en/stable/_images/platformio-ide-vscode-task-explorer-refresh.png) to view the initialisation messages

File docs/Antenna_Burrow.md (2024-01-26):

# Antenna for burrow

This antenna is designed for use on an outdoor burrow, it is suitable with the Tectus RFID reader TITAN 4004 (also know as TLB-30-USB).

<a href="../assets/images/Antennas/burrow_antenna.jpg">
snapshot of the burrow antenna in the lab
</a>

## Radiating pattern

The radiation pattern was measured with a FDX Biolog Tiny Tag from [biolog-animal](https://www.biolog-animal.com/en/products/veterinarian/biolog-tiny-domestic-fauna-10268/)
The read range is 700 mm (typical values) with a FDX transponders (8 mm x 1.4 mm Ø)

<a href="../assets/images/Antennas/burrow_radiation.png">
image of the radiation pattern of the burrow antenna
</a>

## Mechanical specifications

### Dimension

The antenna is a circle of Ø91 mm by 7 mm height. You can access the [mechanical schematic on the repository](https://gitlab.in2p3.fr/rfid.m0/rfid.m0.meca/-/tree/master/antenna_burrow)

### 3D preview

<iframe id="vs_iframe" src="https://www.viewstl.com/?embedded&url=https%3A%2F%2Fgitlab.in2p3.fr%2Frfid.m0%2Frfid.m0.meca%2F-%2Fraw%2Fmaster%2Fantenna_burrow%2FAssembly.stl%3Finline%3Dfalse&orientation=bottom&bgcolor=transparent" style="border:0;margin:0;width:100%;height:400px;"></iframe>

## Electronic specifications

The antenna inductance is around 192µH to be compliant to the Tectus RFID reader TITAN 4004. It is suitable with the 125 - 134 kHz frequency range. It requires 8.8 m of Ø0.2mm enamelled copper wire which would make 30.6 spires (One spire is 0.286 m).

## Assembling instructions

Please refer to the [Developper section of the project for assembling instructions](./Assembling_antenna.md).

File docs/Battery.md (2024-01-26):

# Battery management

## Reload a battery

To reload a battery, preferably use a dedicated battery charger :

1. Select the battery **technology** (Lead or Li-Ion)
2. Select the load mode : **Charge**
3. Select the **number of cells** :
   1. 1 cell for a Li-ion battery (3.6V)
   2. 6 cells for a Lead battery (12V)
4. Define the **load current** : A typical value is C / 3 where C is the capacity of the battery in A.h. In the case a lower current is specified on the battery datasheet, use this value.
   For the lead battery "RS PRO 174-8857", use 1.5A as max current.
5. Start the process by a long press on Start / Enter button
6. The charger will reload the battery according to the program. Wait for the end of the process (beep or visual indication) before disconnecting the battery

## Store a battery

When a battery is planned to be stored for a certain time, you have to set it into **Storage mode** to optimize its lifetime :

1. Connect the battery to the battery charger
2. Select the battery **technology** (Lead or Li-Ion)
3. Select the mode **Storage**
4. Select the **number of cells** and the **max current** : Use the same values as for the reload
5. Start the process by a long press on Start / Enter button

## Documentation

The documentation of the battery and its safety data sheet are available at this [link](./assets/docs/Yuasa 12V lead battery documentation.zip)

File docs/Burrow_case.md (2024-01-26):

# Prepare the burrow case

This page describes how to adapt a Pelicase in order to receive an antenna and user button / indicator.
A **burrow antenna** is required before following these instructions.

- **Drill the left side** of the case according to the [provided drawing](https://gitlab.in2p3.fr/rfid.m0/rfid.m0.meca/-/blob/master/antenna_burrow/Burrow_case_holes.pdf)

<a href="../assets/images/Case/Case_holes.jpg">
Case with holes
</a>

- **Install the antenna** in the Ø16.5mm hole. Ensure the seal is on the outside of the case and maintain the antenna by tightening the brass nut.
- **Install the red led and the push-button** with their own seals and tight them.

<a href="../assets/images/Case/Case_with_components.jpg">
Case with external components
</a>

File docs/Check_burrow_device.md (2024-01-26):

# Check the device

The aim of this page is to describe how to check the device once just assembled.

## Step 1 : Follow the user checking procedure

Start by following the different steps described in the [User Checking Procedure](Checking_procedure.md). Once the tests realized, check the content of the SD card in order to verify :

- Data are written into the SD memory card
- All the events are detected and written (IR events, RFID tag value, system start and shut down...)
- The RTC is up-to-date

## Step 2 : Edit the configuration file

1. Open the CONFIG.cfg file in the SD memory card
2. Edit the option "mode_time_period" to true
3. Edit the option "start_time" by setting an hour higher than the current (in UTC timezone)
4. Edit the option "stop_time" by setting start_time + 2h
5. Save the file and insert the SD card into the device
6. Turn on the device and wait a few minutes
7. Check that the system does not read the sensor by passing a RFID tag into the antenna and checking the external red led does not blink

If this test does not succeed, check the configuration file format is correct (refers to [Configuration](Software_configuration.md) for details).

## Step 3 : Check the battery management

1. Replace the battery by an external power supply and set the voltage (4v for Li-ion device / 13v for lead battery)
2. Turn on the device and wait a few minutes. Then modify the power supply voltage (2.9 for Li-ion device / 11.9v for lead battery)
3. Check that the system is automatically powered-off by passing a RFID tag into the antenna and checking the external red led does not blink. All others leds should also remain off.

If this test does not succeed or if the voltage value is not consistent with your battery, check the parameters **BATTERY_MIN_VOLTAGE** and **POWER_BOARD_BATT_RATIO** into the code.

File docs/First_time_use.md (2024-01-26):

# First time use

## How to use the device?

The antenna must be positioned at the entrance of the burrow so that individuals can pass through. Once the antenna and case are installed, power-on the system and check it's working correctly.

## How to power-on / power-off the device?

Check the battery is connected then press the main switch (with power symbol, pressed = On).
Then press the switch button until the red LED turns on. Once done, release it. The red LED should turn OFF after the startup of the device.

To power-off the device, maintain the switch button pressed until the LED stops blinking and remains on. Once done, press the main switch (released = Off) and disconnect the battery.

## How to check the device is correctly working?

To check the system is working properly after a start-up, refers to the [Checking procedure](Checking_procedure.md)

## How to check the status of the battery?

Quickly press and release the switch button (< 0.5 second). One second after the button release, the red LED will blink from 1 to 5 times : 1 blink per 20% of available battery. Is the red LED is not blinking at all, the system is off.

## How to access to the recorded data?

Once the system off, open the case. Unlock the memory card (one push to lock / unlock the micro-SD card) and get it.
Insert it into a computer and access its contents. Data are stored in text format in files named with date and time (format YY_MM_DD.TXT).

Do not rename SD card files

_NOTE_ The time base is expressed in UTC time period.

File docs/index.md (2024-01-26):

# Home

The rfid.m0 open source project provides the hardware, mechanical and code sources needed for building an embedded system that monitors relatively small species around their shelter.

The devices are gathering an RFID reader to identify TAG individuals, infrared beams to monitor an entrance, and eventually a temperature sensor.
Datas are recorded into an SD card with a timestamp from a real time clock.
Several powering options are proposed from running on standard battery to adding a solar panel.

For instance, two different applications can be applied with the project:

- monitor the burrow occupation of rodent species
- monitor the entrance of a nest box of bird species

Software and electronic sources are shared, mechanical is specific to the application.

## Rodent species device

The rodent species system is contained in a weatherproof case. Easy to transport and install, it can be deployed at the entrance of different burrows.

<a href="./assets/images/User_description/Burrow_device.jpg">
Rodent species device
</a>

## Birds species device

The system for birds species is a device that is mounted in a Schwegler nest box, replacing the existing door. Additionally to the monitoring, an optional door can be automatically closed to capture individuals.

<a href="./assets/images/User_description/Nest_box_device.jpg">
Nest box device
</a>

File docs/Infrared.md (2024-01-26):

# Modulated infrared functionnality

## Description

The infrarer barrier uses the same principle and components than infrared remote controls. A infrared pulsed light is emitted at a certain frequency (36kHz in our case). A receiver, only sensitive to this frequency, is placed in front of the emitter. This receiver sends a low-level output only if it detects the signal (high-level output if no signal).
Indeed this barrier in an On / Off system, with no distance detection. More the infrared signal is intense, higher can be the infrared barrier (several meters).

## Software used to generate a 36 kHz Pulsed Width Modulation

For generating a PWM on the Feather M0, we use the [Arduino SAMD21 turbo PWM](https://github.com/ocrdu/Arduino_SAMD21_turbo_PWM) on an available [PWM pin](./assets/images/Main_board/Feather_M0_pinout.png)

<!-- markdownlint-disable MD010 -->

```C
#include "SAMD21turboPWM.h"         // https://github.com/ocrdu/Arduino_SAMD21_turbo_PWM

#define PIN_IR_PWM      11          // output pwm 36kHz for IR sensor
//...
pinMode(PIN_IR_PWM, OUTPUT);
//...
TurboPWM pwm;
//...
pwm.setClockDivider(16, false);		// Main clock divided by 16 => 3MHz
pwm.timer(2, 4, 20, true);			// Use timer 2 for pin PIN_IR_PWM, divide clock by 4, resolution 20, single-slope PWM
pwm.analogWrite(PIN_IR_PWM, 500);   // PWM frequency is now around 36KHz, dutycycle is 500 / 1000 * 100% = 50%
```

<!-- markdownlint-enable MD010 -->

## PWM 36kHz - output generated

<a href="../assets/images/Main_board/Scope_IR_Modulation_output_1.png">
scope screenshot of 36 kHz modulation for infrared emitter
</a>

Measurement made on the pin output of the Feather M0 without any Infrared emitter connected.

The Infrared emitter has an wide opening angle. For testing purpose, use heat shrink or wrap black tape around it to create a kind of pipe and reduce the opening angle.

## Infrared receiver - input read

<a href="../assets/images/Main_board/Scope_IR_input_1.png">
scope screenshot of infrared photo receiver output
</a>

Measurement made on the pin output of the Phototransistor TSOP34536.

## Examples on the web

- Coutning by IR crossing with Arduino UNO
  <http://makerspace56.org/comptage-par-franchissement-dune-barriere-infrarouge/>

- Youtube "la grotte du geek" with code dedicated for STM32CubeIDE
  <https://www.youtube.com/watch?v=\_tcBtZZDsCE>

- Adafruit "Using an Infrared Library on Arduino"
  <https://learn.adafruit.com/using-an-infrared-library/sending-ir-codes>

## How to check the infrared barriers are working ?

Refers to the [Checking procedure](Checking_procedure.md), section "Infrared beam" to know how to check the IR barrier

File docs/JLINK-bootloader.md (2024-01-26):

# How to restore the Feather M0 bootloader

## In case of problem, reburn the bootloader with J-LINK SWD

**If the --offset was forgotten, the card is not recoverable, even with J-LINK!**

In case of problem with the bootloader, the feather board can be reburned. To do this, it's required to have :

- [the J-Flash program](https://www.segger.com/products/production/flasher/tools/j-flash/about-j-flash/)
- [a J-LINK Debug probe](https://www.segger.com/products/debug-probes/j-link/models/j-link-base/)

The J-LINK Debug probe and the Feather M0 are connected together by an SWD connector on the SWDIO / SWCLK pins (back side of the Feather). Follow the [procedure](https://learn.adafruit.com/proper-step-debugging-atsamd21-arduino-zero-m0/restoring-bootloader) to burn the bootloader.

<a href="../assets/images/Tech_doc/Feather_SWD_pin.jpg">
SWD pinout
</a>

Note: The Feather M0 is write protected. It will be necessary to [write a word to remove the protection](https://hackaday.io/page/5997-programming-a-samd-bootloader-using-jlink-linux).

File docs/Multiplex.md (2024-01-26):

# Multiplex board

This page describes the multiplex board in charge to connect two antennas to the main board.

## Schematic of the system

<a href="../assets/images/Manufacturing/Multiplex_board_schema.svg">
schematic of the multiplex board
</a>

## Materials

### CMOS Analog Switch

<a href="../assets/images/Multiplex_board/AnalogSwitch.png">

</a>

The PI5A100 analog switch allows to multiplex four digital signals up to 5V and 30mA per channel with a 230MHz of bandwith for a low consumption (~10mA).

### Power MOSFET

<a href="../assets/images/Multiplex_board/PowerMosfet.png">

</a>

The IRF540 Mosfet are used to switch the RFID antennas. It accepts signals up to 100V and 33A, while ensuring a low-resistance (~50mOhm) to limit its impact on the RFID antenna range.

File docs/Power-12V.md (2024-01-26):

# Lead-battery power supply board

This page describes the 12v power board, used to connect a 12v lead battery to the device.

## Schematic of the system

<a href="../assets/images/Manufacturing/12V_board_schema.svg">
Kicad schematic of the Power board 12V
</a>

## DC-to-DC converter

The JCE0612S05 DC-to-DC converter provides a 5V output voltage from an input voltage that can varies from **9V to 18V**. It can deliver **1.2A max**.
This component allow to use a battery, whose voltage varies with the state of the charge, as a power source for our device.

Thanks to this converter, the power-board is compatible with several type of batteries : More secured, less sensitive to temperature or fire...

For more information, refers to the [component datasheet](https://www.mouser.fr/datasheet/2/942/SF_JCE06-1508846.pdf).

<a href="../assets/images/Power_board/12v_DC_DC_converter.png">
snapshot of the component JCE0612S05 12V DC to 5V DC
</a>

### Battery

The battery used is a 12V lead battery. Its nominal voltage can reach 14V when fully charged. **Do not unload below 12V.**
During usage, ensure that the temperature is between **0°c to 50°c**.

<a href="../assets/images/Power_board/12v_battery.jpg">
snapshot of the 12V lead battery used Yuasa 5.0 Ah
</a>

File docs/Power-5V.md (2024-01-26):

# Li-Po / Li-Ion battery power supply board

This page describes the 5v power board, used to connect a 3.6v Li-Ion or 3.7v Li-Po battery to the device.

## Schematic of the system

<a href="../assets/images/Manufacturing/5V_board_schema.svg">
Kicad schematic of 5V power board
</a>

## Materials

### Power Boost

<a href="../assets/images/Power_board/5v_PowerBoost.png">
snapshot of the Power Boost 1000 board
</a>

The Power Boost 1000 provides a 5V output voltage from an input voltage that can varies from **1.8V to 5.5V**. It can deliver **1A max**.
This component allow to use a battery, whose voltage varies with the state of the charge, as a power source for our device. The EN pin is used to safely switch On / Off the system.

More information in the [Adafruit tutorial](https://learn.adafruit.com/adafruit-powerboost-1000-basic) and in the [component datasheet](https://www.ti.com/product/TPS61090).

### Solar charger

<a href="../assets/images/Power_board/5v_SolarCharger.png">
snapshot of the BQ24074 solar charger board
</a>

The BQ24074 board allow to manage the charge of a 3.7V Li-Po or 3.6V Li-Ion battery from a solar panel (MPTT solar charge), a DC charger or an USB port. When the solar panel is sunny enough, it powers the system directly to prevent battery from constantly charging/discharging.
The output voltage can fluctuate from **3.7V to 5V** and it can deliver **1.5A max**. Use a **5-10V solar panel** with this power board.

More information in the [Adafruit tutorial](https://learn.adafruit.com/adafruit-bq24074-universal-usb-dc-solar-charger-breakout/overview)

### Solar panel

This 130 x 150 mm solar panel has a power of 2.5W It can deliver 500 mA for a nominal voltage of 5V.

<a href="../assets/images/Power_board/5v_SolarPanel.png">
snapshot a 2.5W 5V solar panel
</a>

### Battery

The battery used is a Lithium-ion battery 3.6V. Its nominal voltage can reach 4.2V when fully charged. **Do not unload below 3V.**
During usage, ensure that the temperature is between **0°c to 50°c**.

<a href="../assets/images/Power_board/5v_battery.jpg">
snapshot of a Li-ion battery
</a>

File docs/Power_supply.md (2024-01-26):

# Power management

According to the choice of battery, two different power boards can be used with the device.
Both boards are physically different but share the same functionnalities.

## Battery voltage measurement

A Li-Po / Li-ion battery voltage can reach 4.2V and a lead-battery 14V. As the Feather M0 do not accept more than 3.3V on its digital inputs, **a voltage divider is required**.
The division ratio is different on the two power board (3 for a 5v power board / 6 for a 12v power board) according to the mounted resistors, and **has to be indicated into the software**.

Some capacitors are also added in order to stabilize the reading. In addition, a moving average filter is performed in the software.

The battery voltage is recorded into the SD memory only if it varies by more than 0.1V since the last record.

## Power-off the system

For a long storage, an On / Off switch physically disconnect the system from the battery.

For a clean power-off, a push-button allow a **controlled power-off** of the system to avoid to corrupt the SD card memory. In addition, the system can also pilot its own power-off in case of overtemperature or low battery voltage.

The method is described into this [tutorial](https://github.com/craic/arduino_power/blob/master/PowerOnPowerOff.md)

<a href="../assets/images/Power_board/power_on_power_off_cycle.png">
explanation steps for power-off functionnality
</a>

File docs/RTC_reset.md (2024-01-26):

# How to reset the Real-Time-Clock without computer

When the RTC loses the time (caused by low voltage of the CR1220 coin cell battery or electromagnetic noise), the led flashes 4 times and the program refuses to start. The normal procedure to correct this issue is to reprogram the system (see [Programming section](./programming.md))

When the programming operation cannot be done (example: in the field without computer access), the RTC can be **set to a default date & time (00h00m00s the January 1st 2099)** so that the program continues to run. Then the clock will increment from that time.

The procedure to do it :

- Turn on the device
- Wait the LED blinks 4 times (indication that an issue occurs with the clock)
- Press the switch button at least 2 seconds : The LED should blink two times to indicate you that the reset is done
- Turn off the device (On / Off button) and restart it

Note : This procedure is only considered if an error with the clock occurs (blink 4 times). If there is no error, a long press will turn off the device (normal behavior).

This operation has to be considered as a back-up option, and the RTC still need to be reprogrammed at the correct date & time when it's possible.

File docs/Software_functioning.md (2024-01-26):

# Functioning of the system

The system checks at regular intervals if the infrared barriers have been broken or restored. If an infrared event has occurred, the RFID sensor is read a number of times (**rfid_attempts** option).

Following this event, and according to the configuration (**mode_capture** option), a capture can be decided.

In case the infrared sensors are disabled, (**opt_IR_1** and **opt_IR_2** options set to false), the RFID reading is continuously done (Caution: this mode consumes a lot of battery).

If the temperature is required (**opt_temp_prec** option set to true), the system measures and records it at regular intervals (**delay_temp** option) only if it has varied by more than 0.02°c since the last record.

The battery voltage is also measured and recorded it if it has varied by more than 0.1V since the last record.

The system can operate all the day or according to an hourly schedule (**start_time** and **stop_time** options). The data (IR event, RFID tag, temperature...) are stored on the SD card with timestamp (UTC time).

## The capture mode

Be aware only advanced user should activate the capture mode! The **mode_capture** option can take a number from 1 to 4 :

1. _Recording of passages_ Following an event on the infrared sensor, RFID reading. No capture.
2. _Capture any individual_ Following an event on the infrared sensor, closing the door.
3. _Capture of specific tags_ Following an event on the infrared sensor, RFID reading. If the tag is one of them described in parameters, closing the door.
4. _Capture untagged individuals_ Following an event on the infrared sensor, RFID reading. If there is no tag, closing the door.

When the capture is decided, the door will be closed after the specified delay (**close_time** option) to let time for the individual to pass.

_Note :_ For each modes, a security timeout opens the door after a certain duration (**release_time** option)

## Security of the system

The device is automatically powered-off if the battery voltage falls below a threshold (BATTERY_MIN_VOLTAGE = 3V for Li-ion battery or 12V for Lead battery)

In addition, if the battery voltage passes below BATTERY_MIN_VOLTAGE + 0.1V, the sensor reading is suspended until the voltage is passed above BATTERY_MIN_VOLTAGE + 0.2V.

The door is automatically opened if :

- it has been closed for a certain duration (**release_time** option)
- system shutdowns in case of under voltage

## Error management

In case of errors, the external red LED turns on and the internal red LED blinks. Acording to the blinking frequency, it's possible to know the error :

- 2 times : Memory card not detected
- 3 times : Failed to write data on the SD card (memory can be corrupted)
- 4 times : Real-Time Clock battery has to be replaced. The program has to be [compiled and uploaded](./programming.md) again to reset the error

## Data description

There are several types of messages written into the SD memory card :

| Data type   | Message content                  | Comment                             |
| ----------- | -------------------------------- | ----------------------------------- |
| System      | Start                            |                                     |
| System      | RTC is ok                        |                                     |
| System      | RTC set time to compilation date |                                     |
| System      | RTC lost power                   |                                     |
| System      | RTC has unknow error             |                                     |
| System      | Sleep mode                       |                                     |
| System      | Wake up mode                     |                                     |
| System      | Up                               | Still alive                         |
| System      | Shutdown : Battery low           |                                     |
| System      | Shutdown : User                  |                                     |
| Ax          | RFID tag                         |                                     |
| IRx         | Broken beam                      |                                     |
| IRx         | Beam restored                    |                                     |
| Temperature | Temperature measurement in °c    | If temp. variation > 0.02°c         |
| Vbat        | Battery measurement in V         | If batt. variation > 0.1V           |
| Vbat        | Power saving                     | Battery < BATTERY_MIN_VOLTAGE + 0,1 |
| Vbat        | Battery restored                 | Battery > BATTERY_MIN_VOLTAGE + 0,2 |
| Vbat        | Battery check by user            |                                     |
| -           | UID mainboard & experiment       | First line of each data file        |
| Door        | Closed                           |                                     |
| Door        | Open : Init                      |                                     |
| Door        | Open : Release time              |                                     |
| Door        | Open : Security                  | High temp, Battery low, Error…      |

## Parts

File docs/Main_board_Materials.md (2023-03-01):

# Main board

## Schéma du circuit d'acquisition

Le système électronique est constitué de composants fonctionnant à différentes tensions:

* 5v (rouge) pour le servomoteur, le module RFiD, le feather M0 et un régulateur 3V3
* 3V3 provenant du feather (marron) qui alimente de manière permanente la RTC
* 3V3 provenant du régulateur (orange) qui alimente émetteurs et récepteurs IR, et le module MAX31865

On distingue les IO en bleu, l'alimentation de la carte en 5V en rouge, et la masse en noir. Plusieurs pins de communication de la carte Feather M0 sont utilisés, notamment les pins de communication I2C pour le RTC, SPI pour le RTD et UART pour le module RFiD.

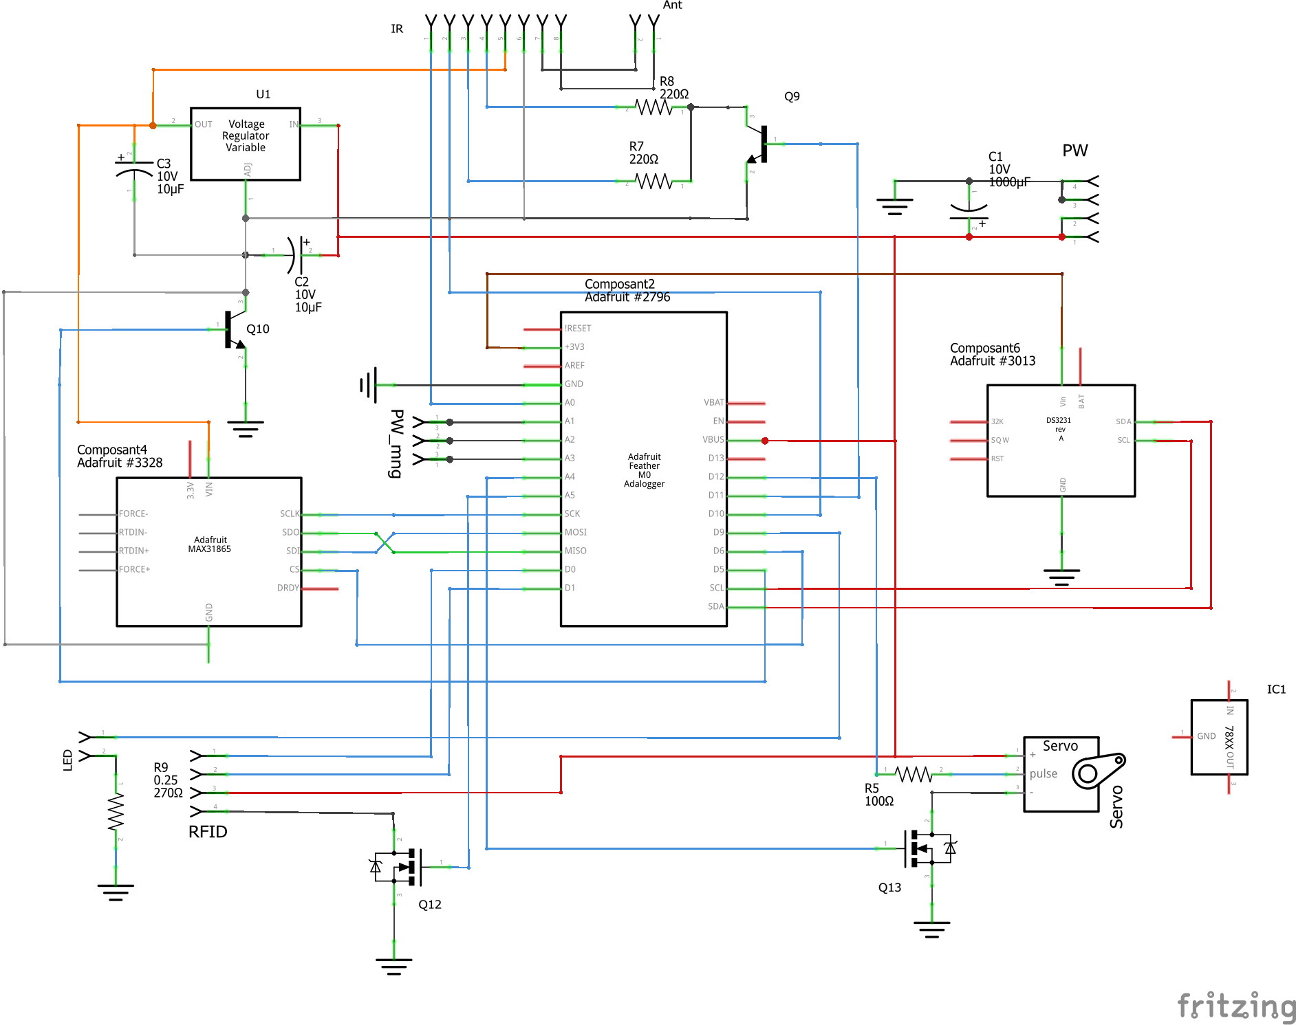
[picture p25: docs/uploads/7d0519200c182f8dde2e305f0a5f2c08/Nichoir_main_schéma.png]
Nichoir_main_schéma


Pour l'alimentation de cette carte d'acquisition se référer à la section [Overview](./Overview.md)

## Materials

### Carte de développement

Picture Feather M0 Adalogger

La Feather M0 Adalogger de Adafruit est une carte de développement de type Arduino spécialement conçue pour des applications d'enregistrement de données. Elle dispose de 256KB de mémoire flash, ce qui lui permet d'avoir un code plus volumineux que la plupart des modèles équivalents. Son slot microSD permet de ne pas manquer d'espace de stockage pour les données recueillies. **Cette carte fonctionne en niveau logique 3.3v, il faut donc faire attention à sa compatibilité avec les capteurs qui fonctionnent en 5v.**

[tutorial adafruit](https://learn.adafruit.com/adafruit-feather-m0-adalogger/pinouts)

### Servomoteur

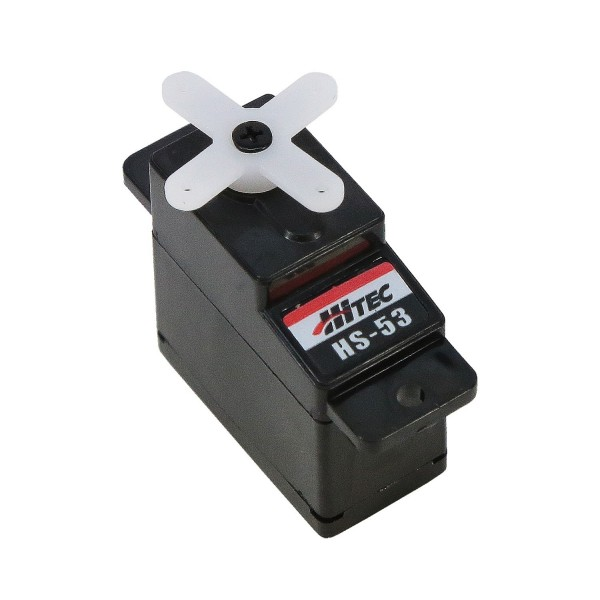
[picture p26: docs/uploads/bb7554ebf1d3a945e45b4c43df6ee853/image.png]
Picture servomoteur


Le servomoteur HS-53 de Hitec est adapté pour des systèmes miniaturisés ou économes en énergie. Sa vitesse de rotation est légèrement supérieure à un tour par seconde. L'alimentation optimale est de 5v, et il est commandé par PWM. Il peut délivrer un couple maximale d'environ 1,5 kg.cm

[Datasheet](https://asset.conrad.com/media10/add/160267/c1/-/gl/001081926ML01/mode-demploi-1081926-mini-servomoteur-analogique-hitec-hs-53-112053-1-pcs.pdf)

### Module RTC

Picture Module RTC

Ce capteur conserve la date, l'heure, les minutes et les secondes grâce à sa pile intégrée. Il nécessite donc une très faible alimentation. En cas de désynchronisation, une fonction du code permet de redéfinir l'instant présent pour l'horloge. Ce capteur communique en I2C. Ici aussi une alimentation 5v est recommandée, mais le capteur fonctionne aussi en 3.3v.

[page produit adafruit](https://www.adafruit.com/product/3013)

[tutorial adafruit](https://learn.adafruit.com/adafruit-ds3231-precision-rtc-breakout/downloads)

### Module RFiD

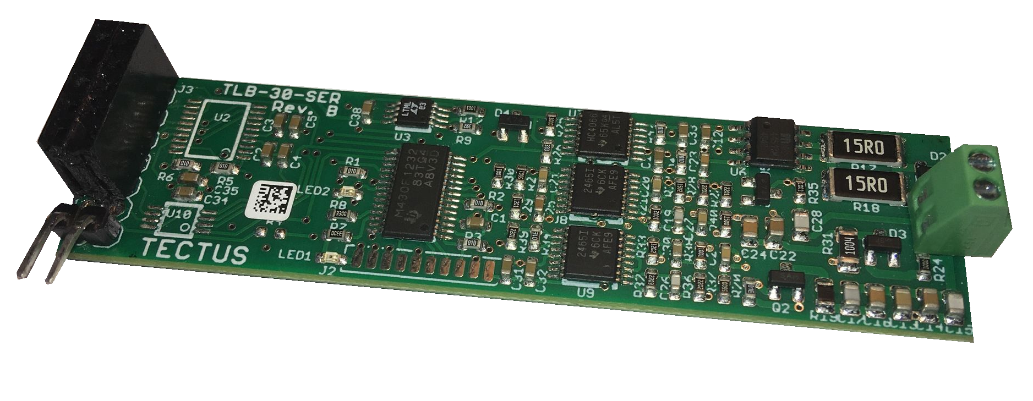
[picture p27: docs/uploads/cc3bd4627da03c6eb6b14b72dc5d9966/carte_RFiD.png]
Picture RFID Board


La carte RFID de tectus supporte les protocoles HDX, FDX et EM4102. Associée à une antenne de 190µH, sa portée dépend surtout de la taille de l'antenne et du transpondeur utilisé.

[pinout Connection drawing.pdf](./uploads/81b7cef750505db74dd9b735ed8705fd/Connection_Drawing_TLB-30-SER.pdf)

[manuel de communication scotty.v1.4_TLB-30-Commands_.pdf](./uploads/651a3e69d9c31fa0e2970c75e4627ca0/scotty.v1.4_TLB-30-Commands_.pdf)

### Capteur RTD

Picture RTD

Le capteur RTD lit la température ambiante grâce à une résistance variable selon la chaleur. Sa plage de température est de 450 à -200 °C. Pour utiliser une sonde à deux fils, on soudera les pastilles *2/3 wire* et *2 wire* et on s'assurera de connecter les fils de l'antenne aux bornes *F+* et *F-*.

[page produit adafruit](https://www.adafruit.com/product/3328)

[tutorial adafruit](TODO)

### Barrière infrarouge

Cette barrière infrarouge modulé à 36kHz filtre les rayonnements infrarouges ambiants naturels, et s'affranchit de la luminosité de l'environnement.

#### Description

La barrière infrarouge utilise le principe et les composants destinés aux télécommandes infrarouges. En effet, on émet une lumière pulsée infrarouge à une certaine fréquence (36kHz). En face on place un photo détecteur qui passe à l'état bas seulement si il détecte un rayonnement IR à cette fréquence. Ainsi Ces capteurs infrarouge fonctionnent en tout ou rien. On ne peut pas régler la distance de détection. Plus le rayonnement Infrarouge est intense plus la barrière infrarouge peut être grande (plusieurs mètres).

#### Émetteur Infrarouge

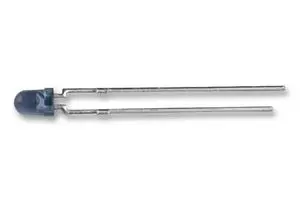
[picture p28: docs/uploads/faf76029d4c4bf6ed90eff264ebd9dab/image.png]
Picture IR emitter


Cathode (-) patte la plus courte (pas de méplat visible)

#### Le code pour établir une PWM à 36kHz

Librairie utilisé [Arduino SAMD21 turbo PWM](https://github.com/ocrdu/Arduino_SAMD21_turbo_PWM)

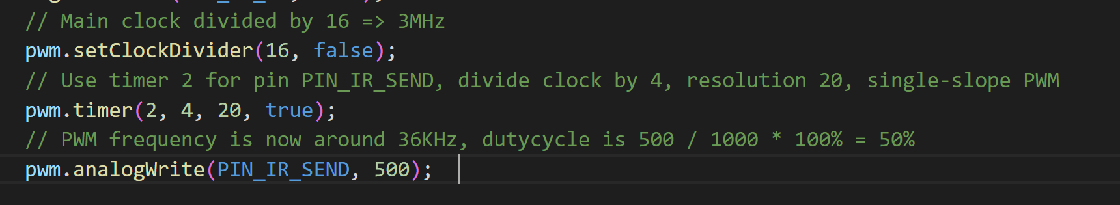
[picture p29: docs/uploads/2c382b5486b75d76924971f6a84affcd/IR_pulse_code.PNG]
IR_pulse_code


#### Phototransistor TSOP34536

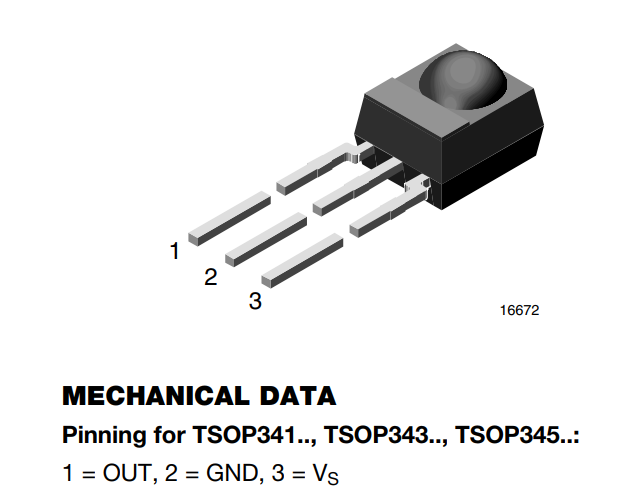
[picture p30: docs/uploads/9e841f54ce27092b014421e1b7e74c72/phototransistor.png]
phototransistor


Alimentation de 2.5V à 5.5V

[datasheet.pdf](https://www.vishay.com/doc?82493)

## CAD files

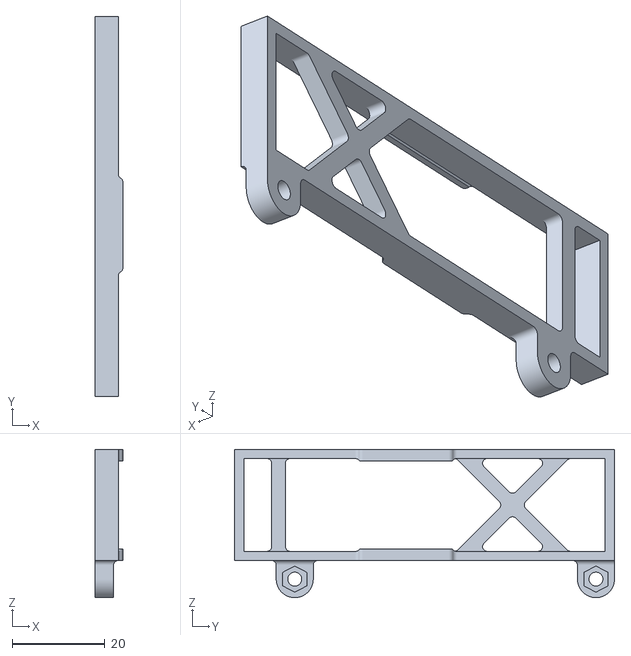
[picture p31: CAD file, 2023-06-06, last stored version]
docs/assets/images/Manufacturing/Support_RFID.stl
6.00 x 82.0 x 32.0

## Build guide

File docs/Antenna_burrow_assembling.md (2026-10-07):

# Make the Coil Antenna and its Metal Sheath

The antenna consists of two main parts:

- **Antenna Base**: Houses the IR sensors and cabling for the RFID antenna.
- **Antenna Cover**: Screws onto the Antenna Base and uses a waterproof seal to ensure a secure fit.

When the Antenna Base and Cover are assembled and the cable is connected, resin casting is applied to protect the sensors.

## Step 1: Prepare the Antenna Base

Refer to the [dedicated page](./Antenna_Burrow.md) for a full description of the antenna and its specifications.

- **3D Print** the part [“Antenna.stl”](https://gitlab.in2p3.fr/rfid.m0/rfid.m0.meca/-/blob/master/antenna_burrow/antenna.stl).
- Apply a **first coat of epoxy resin** to the interior walls of the Antenna Base for impregnation, which will help secure the resin casting. Use a long-setting resin (24 hours) to allow time to fully spread resin along the walls. (Preparation weight ratio: 5 parts resin to 1 part hardener).
- **Wind a Coil Antenna**: Follow the [antenna assembly guide](./Assembling_antenna.md) and wind approximately 30 turns around the Antenna Base to achieve an impedance of 192uH.
- **Connect the IR Emitters and Receivers**: Attach wires (15 cm) to each component, ensuring you follow the [wire color table](#wire_color_table).
- **Secure the IR Components into the Antenna Base**:
  - Position the **IR Emitting Diode** on the left side of the Antenna Base in its designated hole and secure it with a glue gun.
  - Position the **IR Receiver Module** on the right side in its hole, facing outward, and secure it with a glue gun.
  - Apply a polyurethane glue coat (Araldite 2028-1 Spray Gun) inside the IR receiver hole to form a **protective bulb** around the IR Receiver Module. This bulb prevents mud from accumulating over the sensor.

<a href="../assets/images/Antennas/Burrow_ant_base.png">
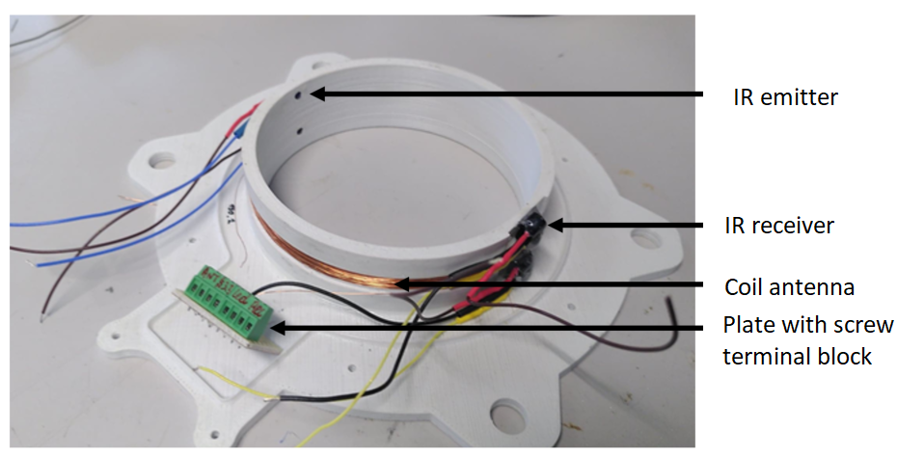
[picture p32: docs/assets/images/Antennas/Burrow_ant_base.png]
Burrow antenna base

</a>

## Step 2: Prepare the Antenna Cover

- **3D Print** the part [“Cover.stl”](https://gitlab.in2p3.fr/rfid.m0/rfid.m0.meca/-/blob/master/antenna_burrow/cover.stl).
- Apply a **first coat of epoxy resin** to the interior walls of the Antenna Cover for impregnation, just as for the Antenna Base. Use the same long-setting resin (24 hours) and preparation ratio (5 parts resin to 1 part hardener).
- **Attach the Short Pipe**: Secure the Short Pipe to the Antenna Cover using an O-ring and a brass nut to create a waterproof seal.

<a href="../assets/images/Antennas/Burrow_ant_cover.png">
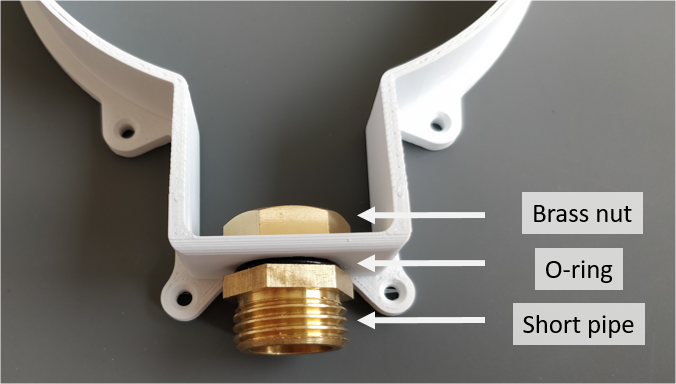
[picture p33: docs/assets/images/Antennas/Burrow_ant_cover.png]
Burrow antenna cover

</a>

## Step 3: Wire the Antenna Assembly

1. **Connect the Antenna Wires**:
   - Connect each antenna wire to the interface board’s terminal block, ensuring correct color-positioning for each wire according to the following color associations:

   | Color        | Function      |
   | ------------ | ------------- |
   | Green        | Receiver IR 1 |
   | White/Green  | Receiver IR 2 |
   | Blue         | Emitter IR 1  |
   | White/Blue   | Emitter IR 2  |
   | Brown        | +3.3V         |
   | White/Brown  | GND           |
   | White/Orange | Antenna +     |
   | Orange       | Antenna -     |
   | Shield       | Linked to GND |

   <a href="../assets/images/Antennas/Burrow_ant_cable.jpg">
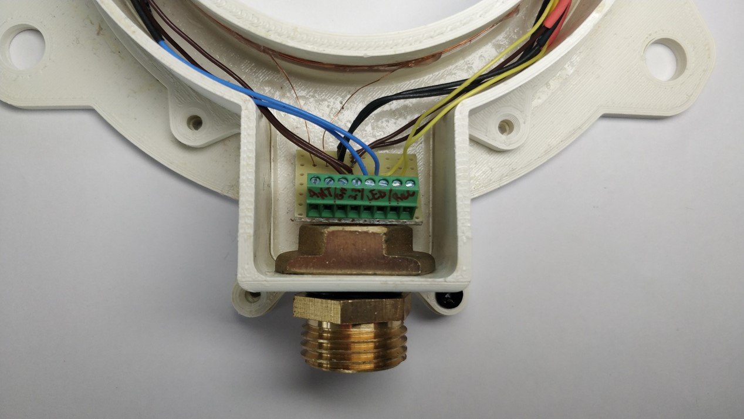
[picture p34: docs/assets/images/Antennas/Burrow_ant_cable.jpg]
Burrow antenna wire
   
   </a>

2. **Prepare the Ethernet Cable**:
   - Strip and tin both ends of the Ethernet cable wires.
   - Screw each wire into the terminal block, following the color associations above.

3. **Check Electrical Resistance**:
   - Measure the resistance between specified points to confirm wiring accuracy. Record the following values for reference:

   | Side +      | Side -       | Electrical Resistance (Ohm) |
   | ----------- | ------------ | --------------------------- |
   | Orange      | White/Orange | ~6 Ω                        |
   | Brown       | White/Brown  | ~6 MΩ                       |
   | Green       | White/Brown  | ~12 MΩ                      |
   | White/Green | White/Brown  | ~12 MΩ                      |
   | Brown       | Blue         | ~18 MΩ                      |
   | Brown       | White/Blue   | ~18 MΩ                      |

4. **Install the Foam Seal**:
   - Insert the foam seal inside the Short Pipe to waterproof the connection.
   - Pass the cable through the Antenna Cover inlet (seal, Short Pipe, and brass nut).

5. **Assemble the Cable Sheath**:
   - Pass the cable through the **Stainless Steel Sheath** and screw it into the Short Pipe.
   - Cut the Ethernet cable to leave 20 cm of excess.
   - Pass the cable through the Long Pipe, and screw the Stainless Steel Sheath onto it.
   - **Attach the O-ring** to the Long Pipe, then secure with a brass nut.
   - **Solder Cable Ends to Male Connectors**: Solder wires to the male connectors in the same order as in the terminal block. Group connectors in sets of four to fit through the brass nut. Ensure the shield wire is connected to ground.

<a href="../assets/images/Antennas/Antenna_extremity.jpg">
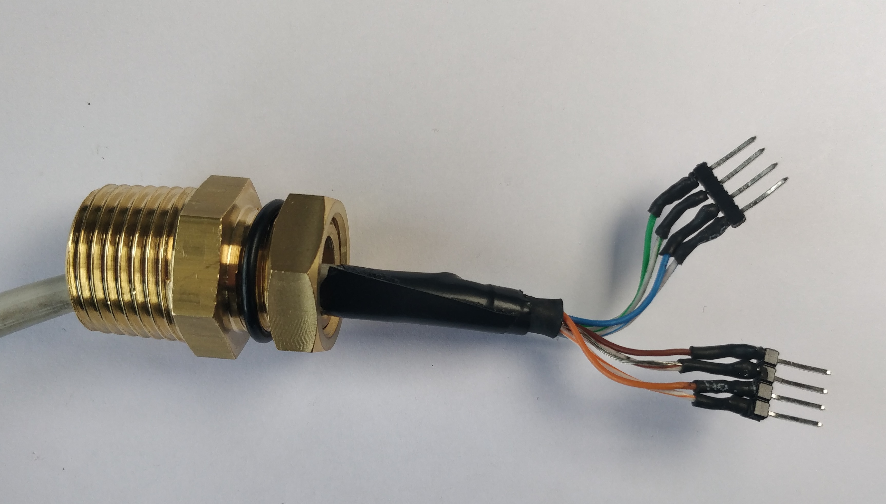
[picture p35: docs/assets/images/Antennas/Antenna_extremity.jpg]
Antenna extremity

</a>

## Step 4: Pour and Cure the Resin

1. **Seal the Cover-Base Junction**:
   - Apply a continuous coat of **LOCTITE SI 595 Superflex transparent silicone** around the cover-base junction to ensure waterproofing.
   - Screw the Antenna Cover onto the Antenna Base using 6mm self-tapping screws. Apply additional silicone as needed to seal any gaps.

2. **Prepare the Antenna for Resin Pouring**:
   - Use modeling clay to cover the IR Emitters and IR Receivers on the inner side of the coil, preventing resin from covering these components.
   - Ensure all cables are positioned inside the antenna. Secure any loose cables with a glue gun to keep them from protruding.

3. **Position the Antenna**:
   - Place the antenna flat and level. Keep the cable upright to prevent shifting as resin cures.

4. **Pour Resin in Two Stages**:
   - **First Pour**: Mix a **20g batch of epoxy resin** (ratio: 2 parts resin to 1 part hardener, with 1% white pigment) to check for leaks.
   - Once the first layer is dry, pour a final **130g batch** of resin with the same ratio to fill the antenna. Allow 24 hours for curing.

5. **Final Clean-Up**:
   - Once the resin is fully cured, remove any remaining modeling clay and excess silicone. Verify the integrity of all seals.

<a href="../assets/images/Antennas/Burrow_ant_resin.jpg">
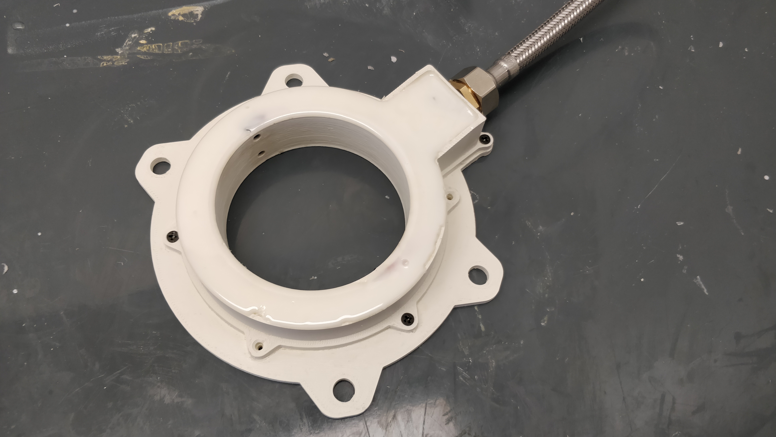
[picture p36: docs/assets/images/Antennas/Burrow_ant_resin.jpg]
Antenna resined

</a>

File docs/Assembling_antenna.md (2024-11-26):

# Assembling a coil antenna

## Bill of Materials

The material needed to make a coil antenna is:

- Enamelled copper wire. The 0.2 copper wire from Radiospares is used ([RadioSpare ref 357-918](https://fr.rs-online.com/web/p/fils-de-cuivre/0357918))
- The structure to wrap the antenna around. This is the 3D printed part named antenna.stl.
- A glue gun
- Standard 28 AWG wire for connecting to the RFID reader
- Soldering material, iron, solder, heat shrink...

## Antenna sizing

If the wire lenght is not specified for the specific antenna we want to build, the Nagaoka's formula would help us.
It returns the inductance based on the coil diameter, the thickness of the wire and the number of spires of the coil antenna.

Note : we are not exactly in the conditions of the formula, the final inductance will need to be measured with an inductance meter.

Two scripts are available for the sizing. The first one calculates the length of wire required for the coil antenna, based on the antenna diameter, the wire diameter and the desired inductance :

??? "Python code for coil inductance sizing"

    ```
    --8<-- "docs/assets/code/Antenna_coil_sizing.py"
    ```

The second script allows to check if the chosen coil design achieves the required inductance, based on the real length and number of spires of the coil :

??? "Python code to check the coil inductance"

    ```
    --8<-- "docs/assets/code/Inductors_characteristics.py"
    ```

## Soldering instructions

The copper wire used is enamelled. For soldering we need first to remove the enamelled coating.
The safest option is to sand the enamel off by using a fine sandpaper.
An other option is to melt the enamel off by using the soldering iron, solder and the flux within it, extra flux.

If you are not used to the method, we strongly recommand to browse for some video of ['How to remove enamel coating from copper wire'](https://www.youtube.com/results?search_query=how+to+remove+enamel+coating+from+copper+wire)

## Assembly steps

- Wrap the wire around its structure. Leave a starting length out of the wrapping, around 20 cm will be ok.
- When the wrapping is done, check the inductance of the coil with an inductance meter. Ensure to select the right frequency (as close as possible to the antenna frequency range).
  The theoretical quality factor of the antenna has to be checked too (Q option on the inductance meter). The Q quality factor can be calculated with the following equation :

$$
Q = \frac{2 \cdot \pi \cdot f \cdot L}{1000 \cdot R}
$$

with Q the quality factor, f the coil frequency in kHz, L the coil inductance in µH, and R the coil resistance in Ohm

- Once the coil is validated, use the glue gun to fix the coil to the structure and wires together
- Prepare the enamelled wire for soldering few centimeters out of the coil. Solder standard wire on it, use heat shrink for insulation. Twist the cable for the antenna tail not to radiate.

<a href="../assets/images/Antennas/Nest_box_antenna_wiring">
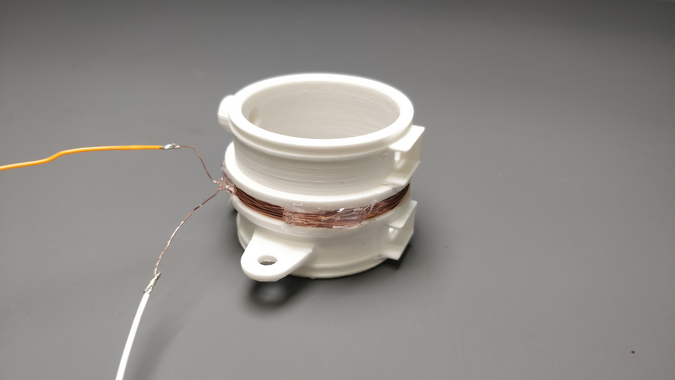
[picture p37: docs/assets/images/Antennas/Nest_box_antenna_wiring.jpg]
Nestbox antenna wired around a 3D printed part

</a>

- Glue the welded parts close inside the 3D printed part

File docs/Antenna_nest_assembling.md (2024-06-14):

# Make the coil antenna

This page describes how to prepare a coil antenna intended to be installed into a nest box.

Refers to the [dedicated page](./Antenna_schwegler.md) for the antenna description with its specifications.

- **3D print** the part « Antenna.stl »
- [Cable a coil antenna](./Assembling_antenna.md) for a 192uH impedance (~67 spires) around the antenna base

<a href="../assets/images/Antennas/Nest_box_antenna_wiring.jpg">
Nestbox antenna wired around a 3D printed part
</a>

- **Cable the IR** emitters and receivers with 28 AWG wire (provide 25cm of free length). Ensure to respect the cable colors :

<a href="../assets/images/Antennas/Nest_box_IR_wiring.jpg">
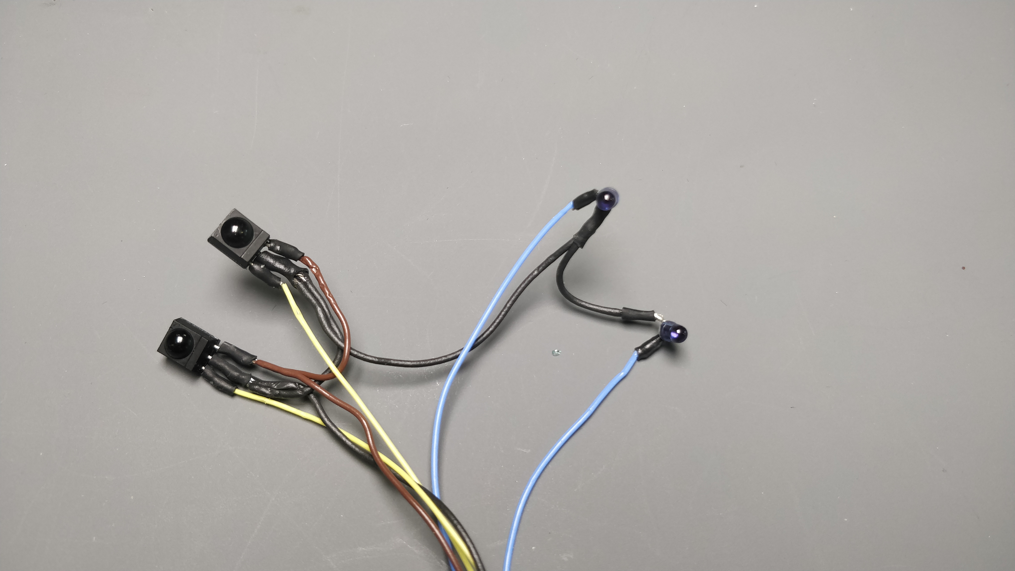
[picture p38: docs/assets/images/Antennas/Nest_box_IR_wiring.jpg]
infrared emitters and photo-receivers wired for 3D printed part

</a>

| Color  | Function      |
| ------ | ------------- |
| Yellow | Receiver IR 1 |
| Yellow | Receiver IR 2 |
| Blue   | Emitter IR 1  |
| Blue   | Emitter IR 2  |
| Brown  | +3.3V         |
| Black  | GND           |

- **Stick the IR** into the antenna :
  - Position the IR Emitting Diode on the left side, seated in the hole and block it with glue gun
  - Position the IR receiver module on the right side, face to the hole and block it with glue gun.

<a href="../assets/images/Antennas/schwegler_antenna.jpg">
wired antenna and infrared beams around the 3D print in the lab
</a>

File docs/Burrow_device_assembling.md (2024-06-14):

# Final assembling

This page describes how to assemble all the burrow device components into a Pelicase.

Some supports are prepared and then the electronic boards are mounted on it and wired. Finally the equipped supports are installed into the Pelicase and connected to the antenna and the batteries.

To follow these steps, it's required to have already realized a [burrow antenna](Antenna_burrow_assembling.md), all the [electronic boards](Electronic_assembling.md) and a [burrow case](Burrow_case.md).The main board has to **be [programmed](programming.md) and RTC has to be up-to-date**. In addition, the **burrow antenna has to be attached** to the case.

## Step 1 : Prepare the supports

- 3D print the part ["RFID_support.stl"](https://gitlab.in2p3.fr/rfid.m0/rfid.m0.meca/-/blob/master/antenna_burrow/RFID_support.stl)
- Insert 2 x M2 nuts in the RFID support
- Insert the RFID reader in its support. Be careful to respect the orientation

<a href="../assets/images/RFID/RFID_wSupport.jpg">
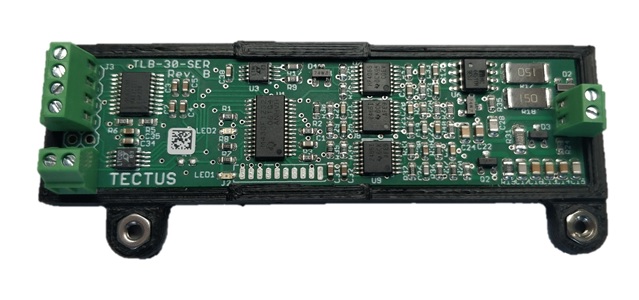
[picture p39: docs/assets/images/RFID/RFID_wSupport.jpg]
RFID reader in its support

</a>

- Prepare the PVC fixation parts ["Lower_support"](https://gitlab.in2p3.fr/rfid.m0/rfid.m0.meca/-/blob/master/antenna_burrow/Lower_support.pdf) and ["PCB_support"](https://gitlab.in2p3.fr/rfid.m0/rfid.m0.meca/-/blob/master/antenna_burrow/PCB_support.pdf) according to their drawings
- Screw two angle brackets into the "Support_inf" plate with 4 self-tapping screws M3 x 6

<a href="../assets/images/Burrow_assembling/Lower_support.jpg">
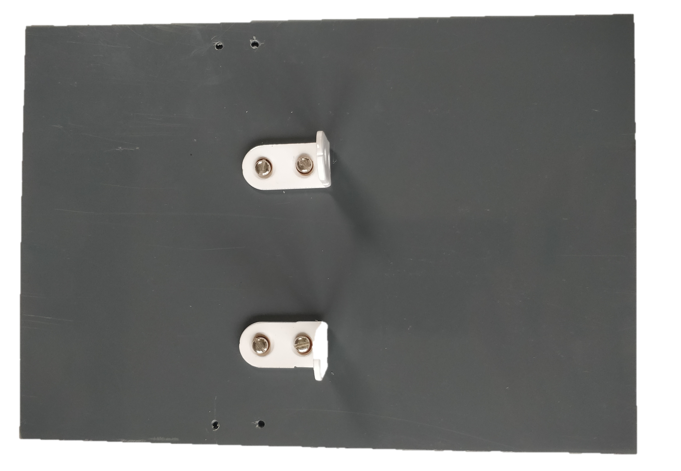
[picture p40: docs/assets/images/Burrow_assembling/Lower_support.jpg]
Lower support

</a>

## Step 2 : Assembly the PCB support

- Attach the main board on the "Support_PCB" plate using 2 x M2 x 12 screws and M2 nuts into the top holes. Do not tighten
- Position the RFID reader and its support on the back side of the "Support_PCB" plate. The right hole of the RFID support has to be faced the holes of the main board
- Add 1 x M2 x 10 screw into the bottom hole of the main board, through the "Support_PCB" plate, and screw them into the RFID support
- Add 1 x M2 x 10 screw into the remaining hole of the RFID support
- Tight the 4 screws
- Add the power board 12V on the back side of the "Support_PCB" plate, facing the two top screws of the main board
- Add 2 x M2 nuts and tight them

<a href="../assets/images/Burrow_assembling/PCB_support_noWire.jpg">
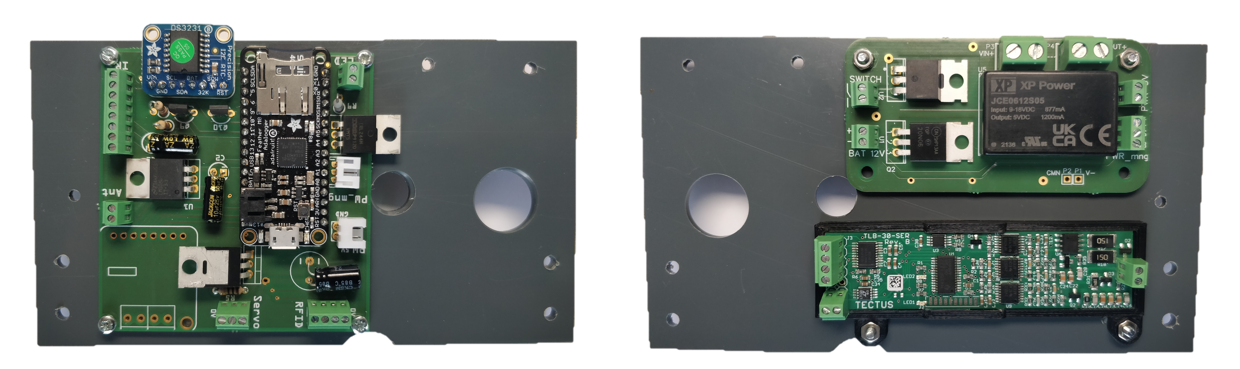
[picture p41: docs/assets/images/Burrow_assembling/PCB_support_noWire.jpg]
PCB support assembling without wires

</a>

- Add and screw 6 wires from RFID reader to the main board
- Connect the 3 ways JST PH cable (cable delivered with the 3 ways JST PH connector) into the main board and wire it into the power board 12V connector (PWR_mng connector)
- Connect the 2 ways JST XH cable into the main board and wire it into the power board 12V connector (PWR_5V connector)
- Connect two wires into the main button with two lugs
- Maintain the SWITCH button into the "Support_PCB" by 2 x M2.5 x 20 screws, 2 washers and 2 x M2.5 nuts
- Connect the wire extremity to the "SWITCH" connector of the power board

<a href="../assets/images/Burrow_assembling/PCB_support_Wire.jpg">
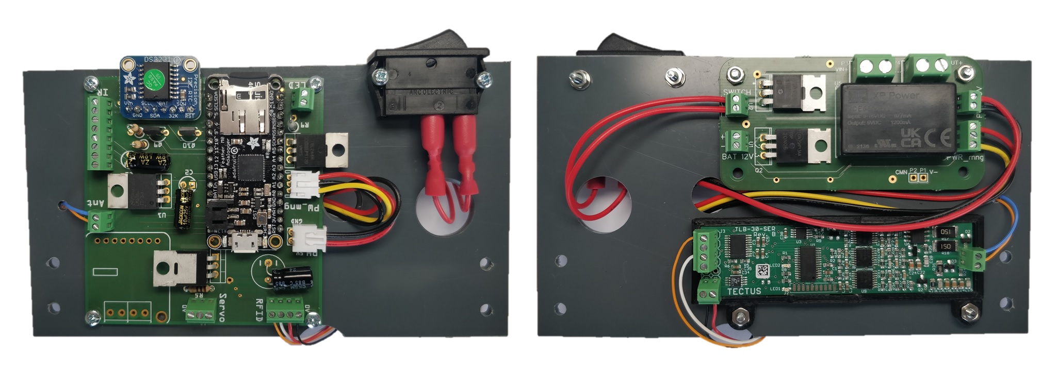
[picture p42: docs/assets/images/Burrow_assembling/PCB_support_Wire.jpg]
PCB support assembling with wires

</a>

- Screw two angle brackets into the "Support_PCB" plate with 4 x M3 x 8, M3 washers and M3 nuts. Angle brackets have to be positioned on the RFID side of the plate.

## Step 3 : Assembly the case

- Wire the START button with two pairs of wires : Each pair have to be connected on the NO & COM pins.
  _Note_ It's advised to **wind the wires of each pairs together** in order to correctly wire them next into the main board
- Install the "Support_inf" plate into the case
- Insert the antenna connector into the main board screw terminal block and tight. **Ensure the IR receiver module #1 (green wire) is positioned at the top**
  _Note_ The antenna connector has to be screwed into the main board **before the "Support_PCB" plate fixation** into the case, for a better access to the screws
- Screw the red led into the 2 ways screw terminal block of the main board

<a href="../assets/images/Burrow_assembling/Terminal_wiring.jpg">
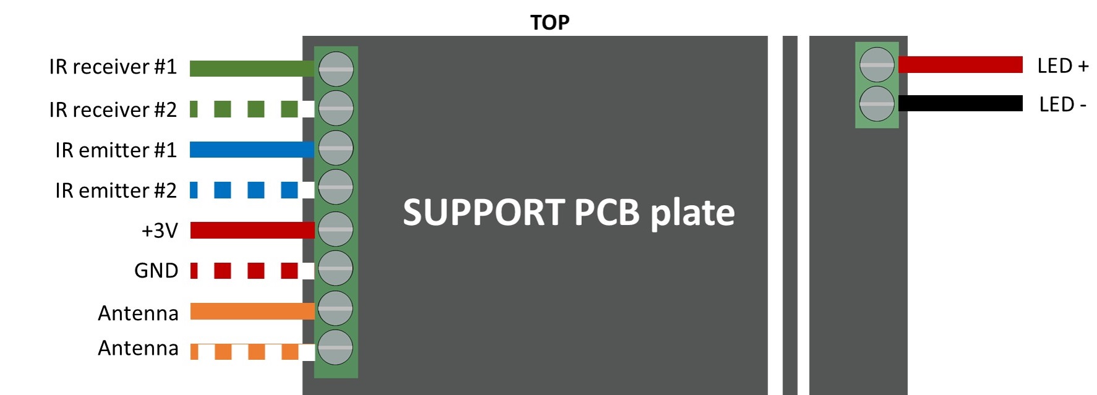
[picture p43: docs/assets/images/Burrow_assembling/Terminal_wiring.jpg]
Terminal wiring

</a>

- Screw the "Support_PCB" plate into the "Support_inf" plate with 4 self-tapping screws M3 x 6
- Pass the START button cables through the "Support_PCB", and connect it to the terminal blocks of the power board 12V
- Prepare two power supply cables of 15cm, with lug at one extremity, and connect the other extremity in the "BAT 12V" connector of the power board

<a href="../assets/images/Burrow_assembling/Final_wiring01.jpg">
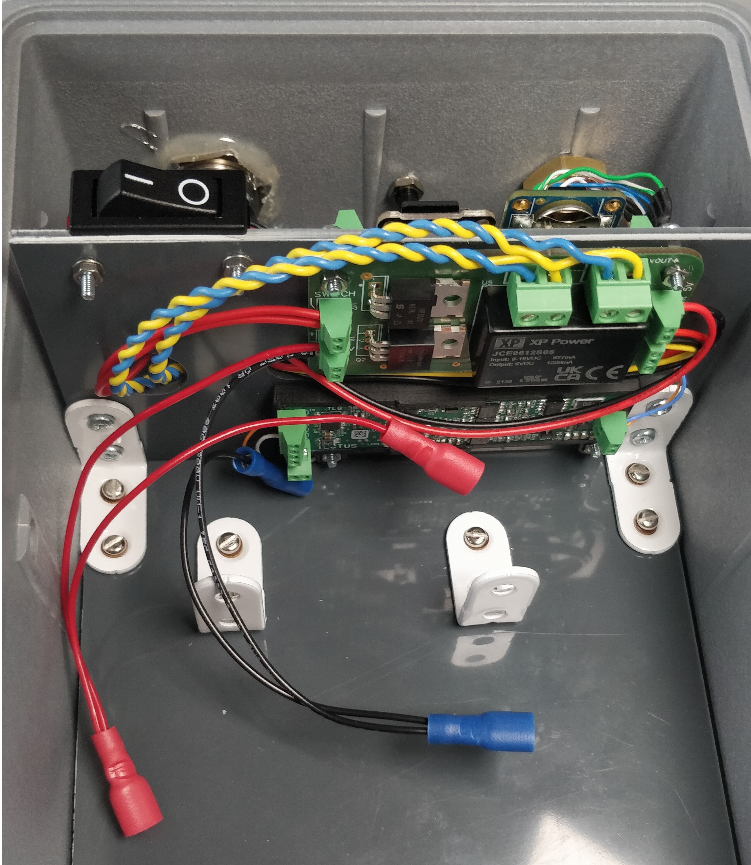
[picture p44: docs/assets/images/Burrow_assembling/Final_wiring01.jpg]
Final wiring

</a>
<a href="../assets/images/Burrow_assembling/Final_wiring02.jpg">
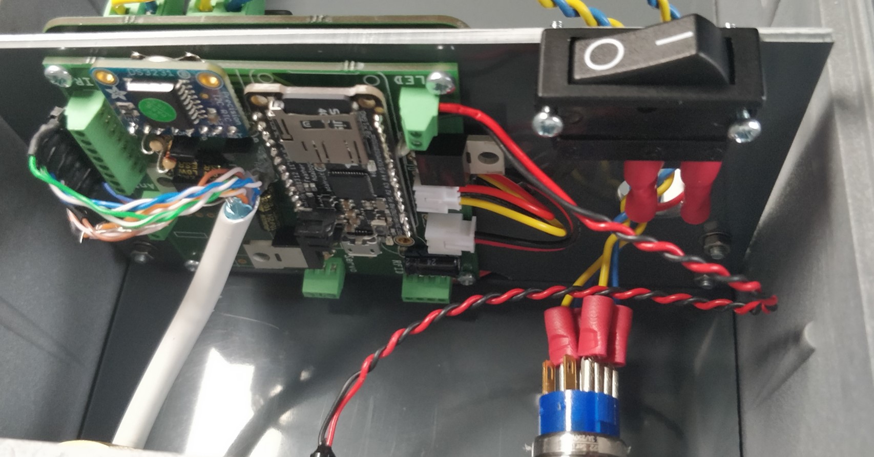
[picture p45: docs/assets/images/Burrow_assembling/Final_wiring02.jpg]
Final wiring

</a>

- Add 5 mm thick sealing tape on each side of the battery compartment
- Add 3 mm thick sealing tape above the battery slot
- Add the batteries and connect them with the dedicated lugs

<a href="../assets/images/Burrow_assembling/Final_assembling.jpg">
Final assembling
</a>

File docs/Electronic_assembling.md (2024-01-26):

# Electronic

This page describes how to prepare the three electronic boards required by the device.

Firstly a main board is assembled to receive the different components and connectors. Secondly, some terminal blocks are added to the RFID board in order to be easily connected with the other boards. Finally, a power board is assembled according to the choice of battery (5v or 12v battery).

Optionally, a multiplex board can be assembled in order to connect two antennas to the main board.

## Step 1 : Prepare the main board

- Weld the different screw terminal blocks into the board, as the two JST connectors
- Add the RTC module : Ensure to **mount the coin cell battery on the top side**
- Add the Feather M0
- (Optionally) Add the temperature sensor
- Insert the CR1220 battery the corresponding slot of the RTC module
- Insert a microSD card in the corresponding slot of the SD module

<a href="../assets/images/Main_board/Final_assembling.jpg">
Main board final_assembling
</a>

## Step 2 : Prepare the Tectus RFID reader

- Weld a 2 ways screw terminal block on the right extremity of the RFID board
- Weld a 2 ways screw terminal block on the bottom holes of the RFID board
- Weld a 4 ways screw terminal block on the top left holes of the RFID board

<a href="../assets/images/RFID/RFID_board.jpg">
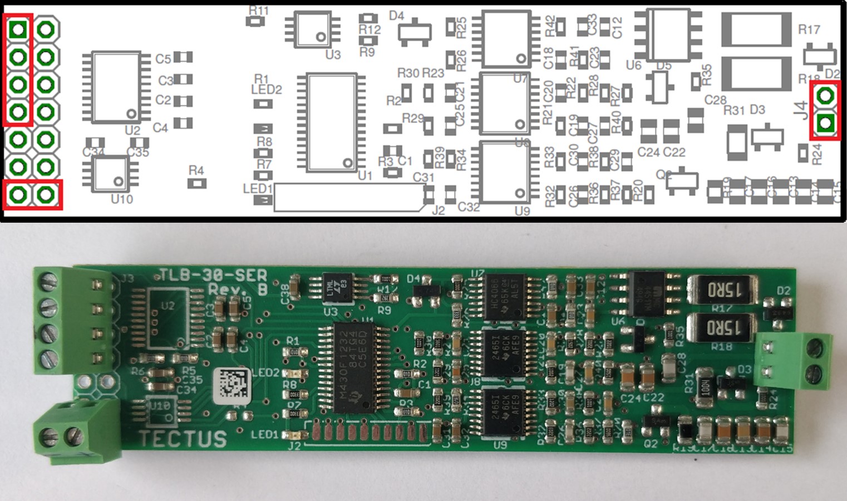
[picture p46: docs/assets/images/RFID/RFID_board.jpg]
RFID board with connectors

</a>

## Step 3 : Prepare a power-supply board

According to the power supply available, two different boards can be prepared :

### 5V power supply board

- Prepare the Powerboost and the Universal charger by assembling them
- Weld the Powerboost
- Weld the Universal charger
- Add the different screw terminal blocks
- Complete the power board by adding the 1000µF capacitor (not represented in the picture)

<a href="../assets/images/Power_board/5v_powerSupp.jpg">
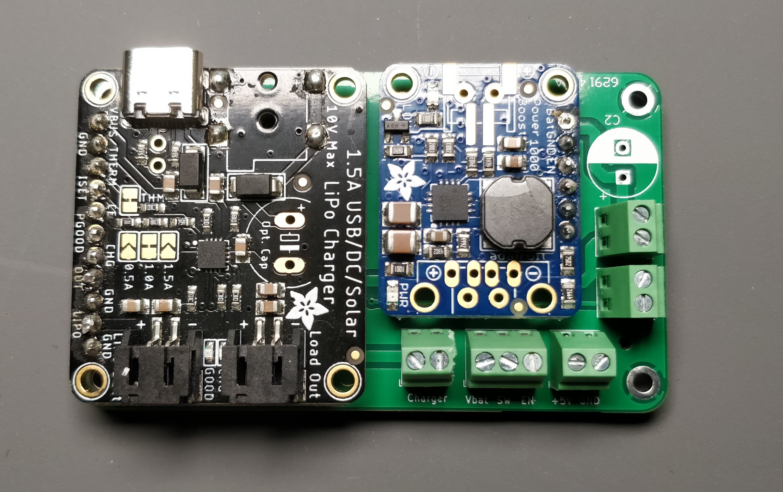
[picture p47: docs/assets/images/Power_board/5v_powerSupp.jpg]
5v power supply

</a>

### 12V power supply board

- Weld the screw terminal blocks
- Weld the 5V DC-to-DC converter

<a href="../assets/images/Power_board/12v_powerSupp.jpg">
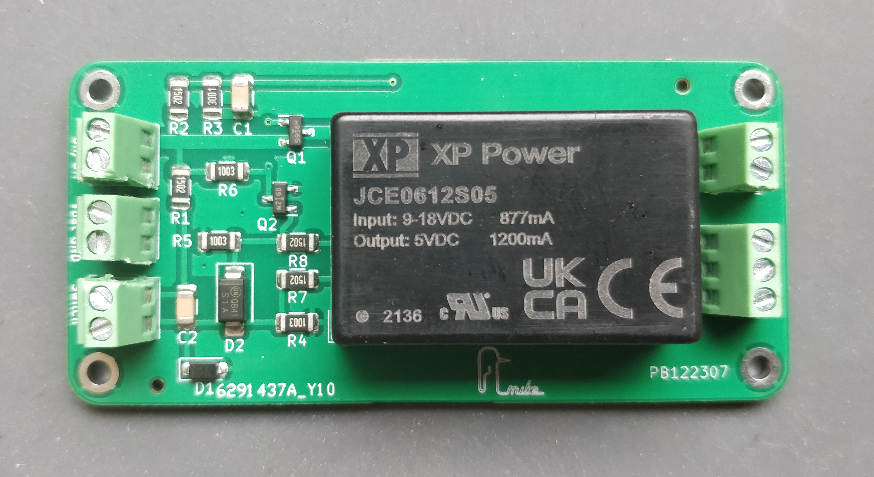
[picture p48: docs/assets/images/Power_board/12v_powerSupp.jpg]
12v power supply

</a>

## Step 4 (optional) : Prepare a multiplex board

- Weld the screw terminal blocks : 3 x 8 screw and 1 x 3 screws
- Add the 5v DC-to-DC converters (not represented in the picture)

<a href="../assets/images/Multiplex_board/Multiplex_board.jpg">
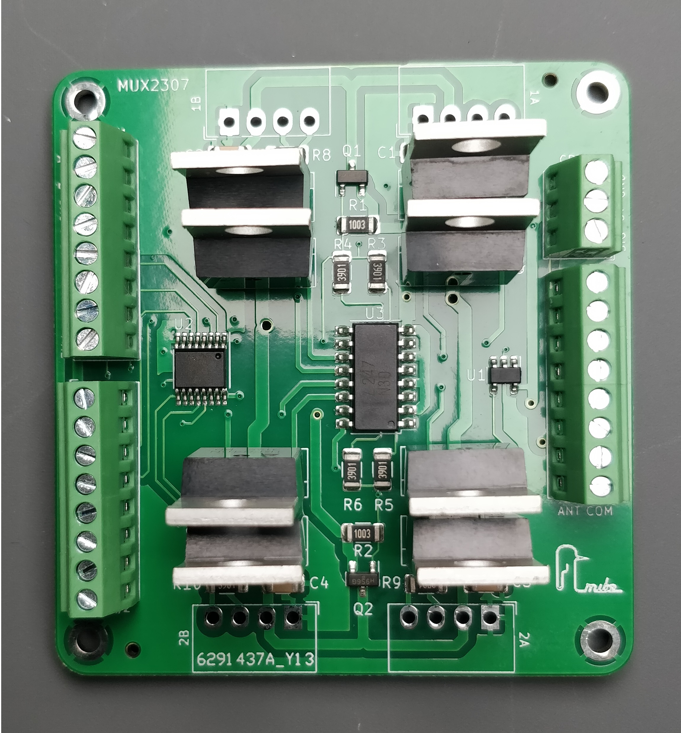
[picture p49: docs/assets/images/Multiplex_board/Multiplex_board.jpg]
multiplex board

</a>

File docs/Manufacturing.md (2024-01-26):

# Manufacturing files

All the required files for the manufacturing are accessible at these links :

- [Electronical repository](https://gitlab.in2p3.fr/rfid.m0/rfid.m0.elec)
- [Mechanical repository](https://gitlab.in2p3.fr/rfid.m0/rfid.m0.meca)
- [Software repository](https://gitlab.in2p3.fr/rfid.m0/rfid.m0.code)

You can also directly [Download as zip](https://gitlab.in2p3.fr/rfid.m0/rfid.m0.elec/-/archive/master/rfid.m0.elec-master.zip)

The bill of materials of required material is avaible at this [BOM link](https://gitlab.in2p3.fr/rfid.m0/rfid.m0.elec/-/raw/master/BOM_append.xlsx?inline=false).

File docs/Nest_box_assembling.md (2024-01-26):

# Final assembling

This page describes how to assembly mechanical & electronic components dedicated to a nest box. Some 3D printed supports are prepared and then the electronic boards are inserted and fixed into it.

To follow these steps, it's required to have already realized a [nest box antenna](Antenna_nest_assembling.md) and the [electronic boards](Electronic_assembling.md).The main board has to **be [programmed](programming.md) and RTC has to be up-to-date**.

## Step 1 : 3D print the parts

- Case : [Upper_case.stl](https://gitlab.in2p3.fr/rfid.m0/rfid.m0.meca/-/blob/master/antenna_schwegler/3D_print/Full_device/Upper_case.stl) and [Lower_case.stl](https://gitlab.in2p3.fr/rfid.m0/rfid.m0.meca/-/blob/master/antenna_schwegler/3D_print/Full_device/Lower_case.stl)
- Technical door : [Technical_door.stl](https://gitlab.in2p3.fr/rfid.m0/rfid.m0.meca/-/blob/master/antenna_schwegler/3D_print/Full_device/Technical_door.stl)
- RFID support : [RFID_support.stl](https://gitlab.in2p3.fr/rfid.m0/rfid.m0.meca/-/blob/master/antenna_schwegler/3D_print/Full_device/RFID_support.stl)
- Battery case : [Battery_case.stl](https://gitlab.in2p3.fr/rfid.m0/rfid.m0.meca/-/blob/master/antenna_schwegler/3D_print/Full_device/Battery_case.stl)
- Battery cover : [Battery_cover.stl](https://gitlab.in2p3.fr/rfid.m0/rfid.m0.meca/-/blob/master/antenna_schwegler/3D_print/Full_device/Battery_cover.stl)
- Trap lever : [Trap_lever.stl](https://gitlab.in2p3.fr/rfid.m0/rfid.m0.meca/-/blob/master/antenna_schwegler/3D_print/Full_device/Trap_lever.stl)
- Trap door : [Trap_door.stl](https://gitlab.in2p3.fr/rfid.m0/rfid.m0.meca/-/blob/master/antenna_schwegler/3D_print/Full_device/Trap_door.stl)

## Step 2 : Prepare the case

- Solder the main button switch (bistable) and the switch button (monostable) to free wire end : Let ~10cm and ~20cm of wire respectively.
- Solder the USB connecter to a JST connector. let ~15cm of wire
- Install the two buttons on the lower case. Add two switch sealing boots with their seals.
- Install the USB connector and its seal
- Install the red led and its seal on the lower case

<a href="../assets/images/Nest_box_assem/Nest_box_bottom.jpg">
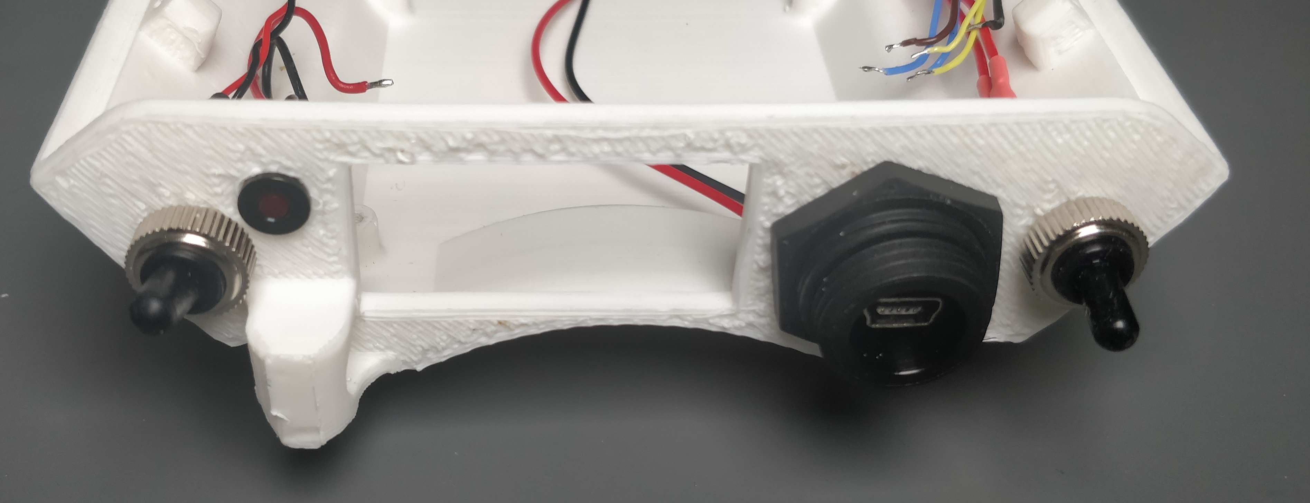
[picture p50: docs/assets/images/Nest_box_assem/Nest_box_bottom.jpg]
Nest box bottom

</a>

- Install one O-rings Ø36mmx1 on each extremity of the antenna
- Install the antenna into the lower case and fix it with 2 x M2 L6 screws

<a href="../assets/images/Nest_box_assem/Nest_box_wAntenna.jpg">
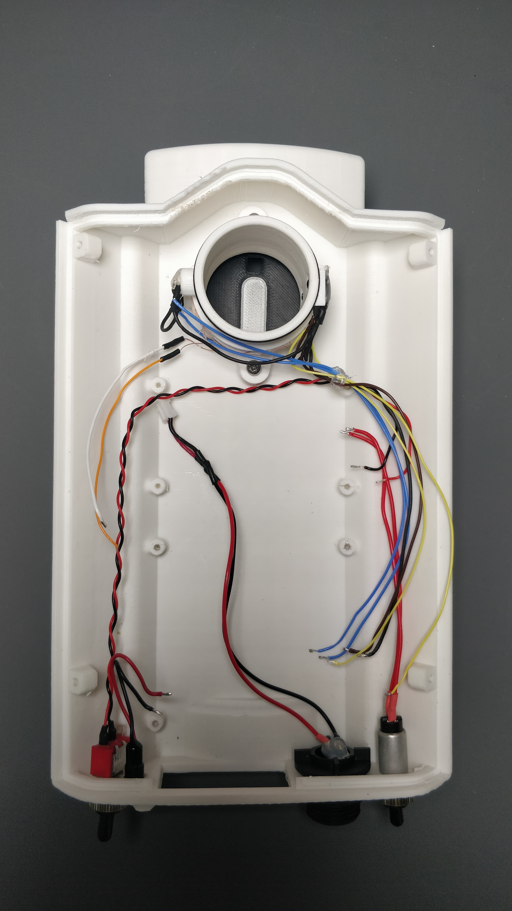
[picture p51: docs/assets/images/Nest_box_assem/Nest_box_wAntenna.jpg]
Nest box empty with antenna

</a>

## Step 3 : Add electronic boards & wiring

- Install the power board into the lower case and fix it with 2 x M2 L8 screws + 2 x M2 L10 screws
- Connect the USB wires to the 'Batt' connector of the solar charger
- Connect the switch button to the 2 ways screw terminal block 'SW'
- Connect the main button switch to the 2 ways screw terminal block 'On / Off'

<a href="../assets/images/Nest_box_assem/Power_board_installed.jpg">
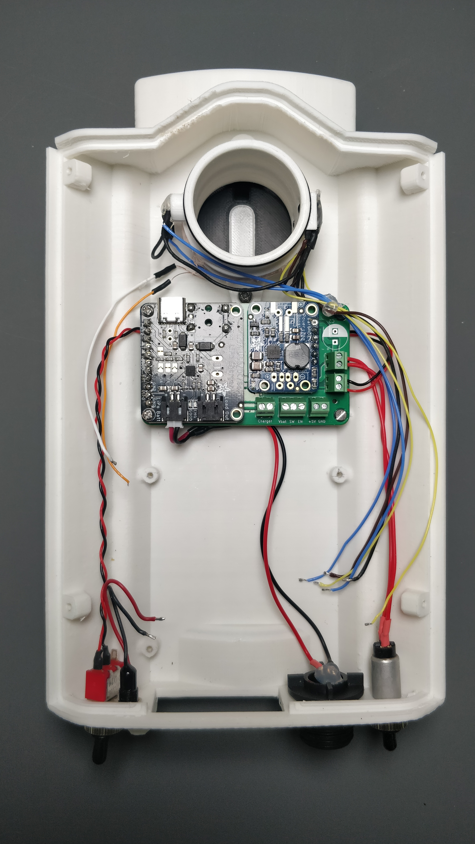
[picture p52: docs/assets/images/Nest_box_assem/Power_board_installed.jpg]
Installation of power board

</a>

- Install the main board into the lower case and fix it with 1 x M2 L8 screws into the left bottom hole
- Connect the 3 ways JST XH cable (cable delivered with the 3 ways JST XH connector) into the PWR_mng connector, and the other extremity of this cable to the power board (connector BAT / EN / SW)
- Connect the 2 ways JST XH cable into to the PW connector, and the other extremity of this cable to the power board (connector +5V / GND)
- Connect the LED to the main board into the LED connector
- Connect the cable from the antenna into the 8 ways screw terminal block. **Do not connect the RFID antenna**. Ensure to connect the photoreceptor at the top of the antenna into the PR1 screw terminal block, and the one of the bottom into the PR2 block.
- Connect the RFID connector to free wire end : Let ~10cm of wire

<a href="../assets/images/Nest_box_assem/Main_board_installed.jpg">
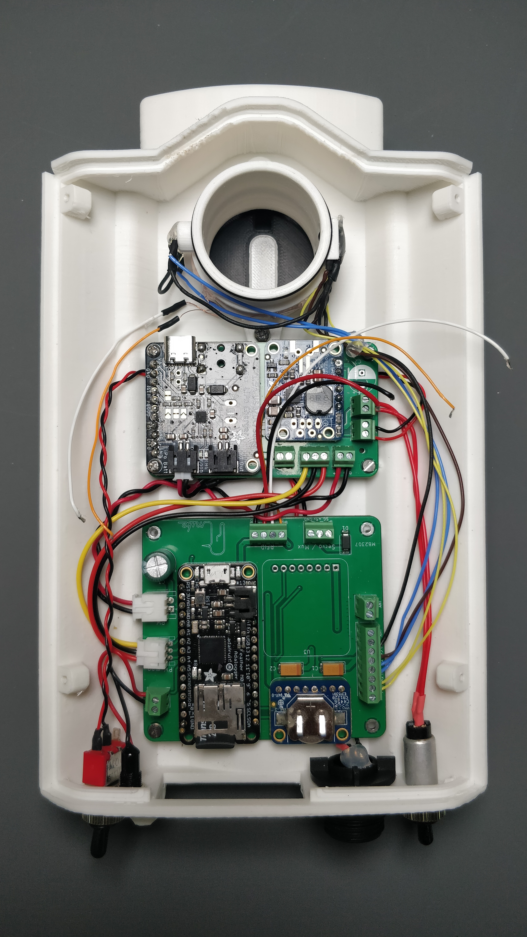
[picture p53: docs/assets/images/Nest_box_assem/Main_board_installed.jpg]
Installation of main board

</a>

- Install the Tectus RFID board into its 3D-printed support
- Connect the coil antenna to the antenna connector of the Tectus board
- Connect the Tectus RFID board to the main board
- Once all the wires connected, fix the RFID support to the lower case by 2 x M2 L20 screws, through the main board

<a href="../assets/images/Nest_box_assem/Nest_box_opened.jpg">
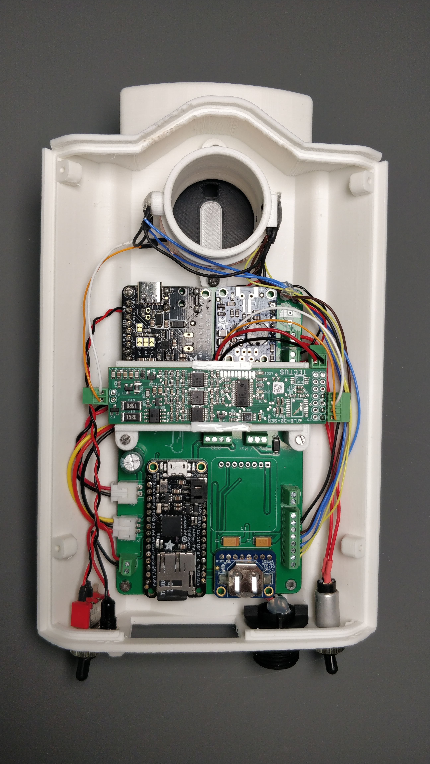
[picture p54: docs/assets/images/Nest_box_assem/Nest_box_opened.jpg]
Nest box assembled opened

</a>

## Step 4 : Close the case

- Add some Loctite SI5940 Sealant to the joint surface, all around the lower case. Wait about 1h for it dry before moving to the next operation

<a href="../assets/images/Nest_box_assem/Nest_box_opened_seal.jpg">
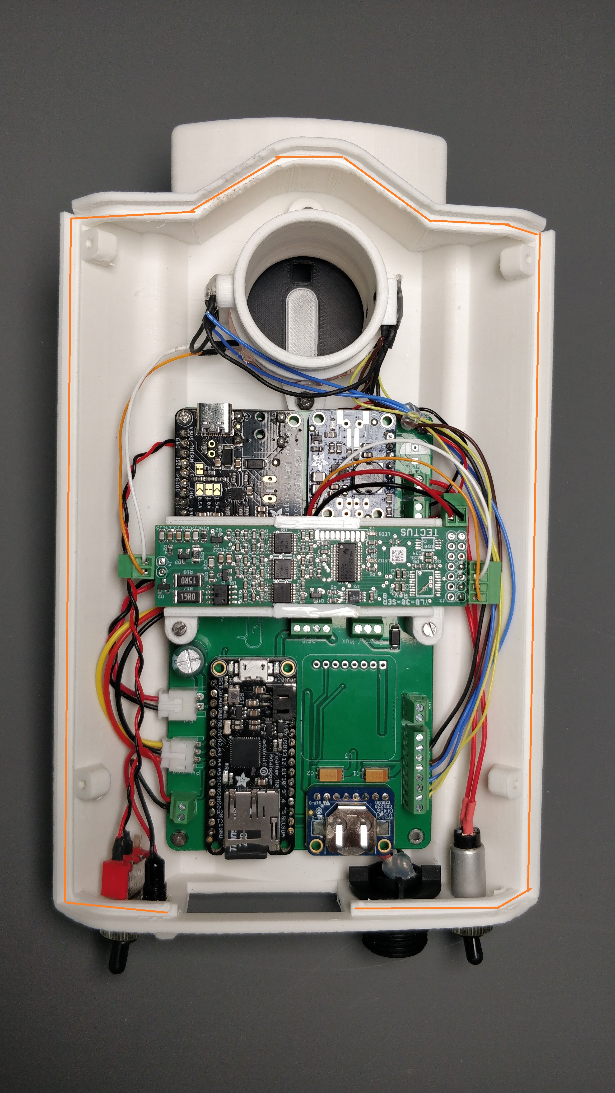
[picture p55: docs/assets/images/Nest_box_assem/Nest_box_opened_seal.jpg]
Nest box assembled opened with seal

</a>

- Close the nest box and fix it with 4 x M2.5 L6 countersunk screws
- Add the trap door, the trap lever and its elastic
- Add the technical door

<a href="../assets/images/Nest_box_assem/Nest_box_closed.jpg">
Nest box assembled
</a>

## Step 5 : Add the battery

- Solder the battery to the USB cable
- Install the battery into the battery case
- Add the battery cover
- Close the assembly with 4 x M2 L10 screws
- Connect the USB cable into the USB connector

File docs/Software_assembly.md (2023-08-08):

# Software assembly

The device is composed by several sub-systems : electronic board, sensors, software, experiment... In order to ensure the traceability of equipment and data, an assembly file resumes the unique identifier (UID) of each sub-system.

Each measurement data is then recorded with the associated sensor UID. In addition the UID of the main board and the experiment is recalled at the beginning of each data file.

## Assembly file

The device assembly is described in the assembly file "ASSEMBLY.cfg" located on the SD card.

??? "Assembly file with example values"

    ```
    {,
    "uid_powerboard":"PB202303001",
    "uid_tectus":"202124001",
    "uid_rfid_sensor":"2303002591056",
    "uid_software":"rfid.m0.code.2.0.0-rc.2",
    "uid_experiment":"202303YH001"
    }
    ```

The file is written as a [JSON string](https://developers.squarespace.com/what-is-json), take care to keep quotes and commas intacts when modifying the file.

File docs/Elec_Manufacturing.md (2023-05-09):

<!-- markdownlint-disable MD033 -->

# Manufacturing files

All the required files for the manufacturing are accessible at this link : [Access to the Repository](https://gitlab.in2p3.fr/rfid_m0/rfid_m0.elec)

You can also directly [Download as zip](https://gitlab.in2p3.fr/rfid_m0/rfid_m0.elec/-/archive/master/rfid_m0.elec-master.zip)

The list of required material is avaible at this [link](./assets/images/Manufacturing/Bill of material.xlsx).

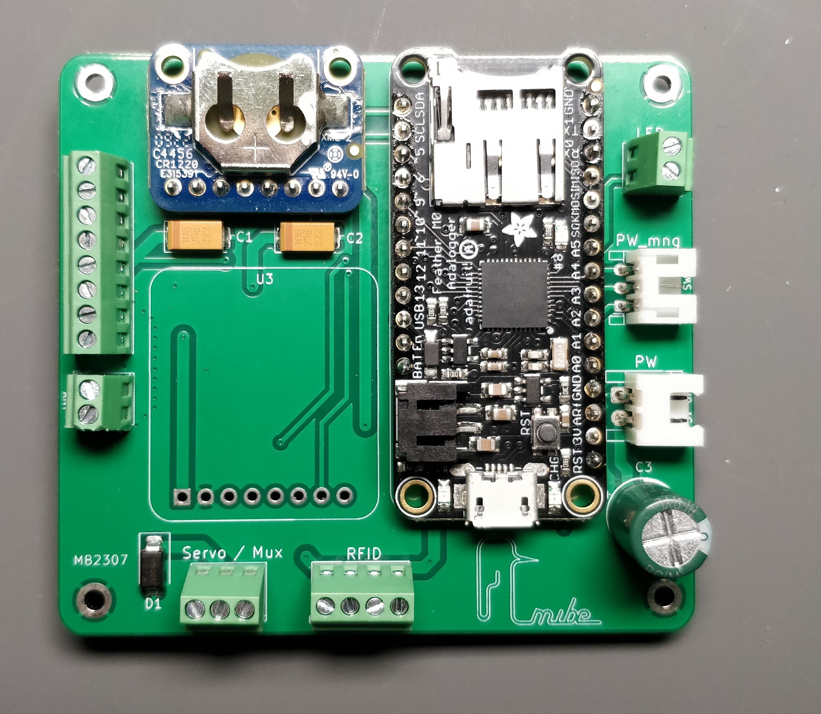
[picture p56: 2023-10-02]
docs/assets/images/Main_board/Final_assembling.jpg

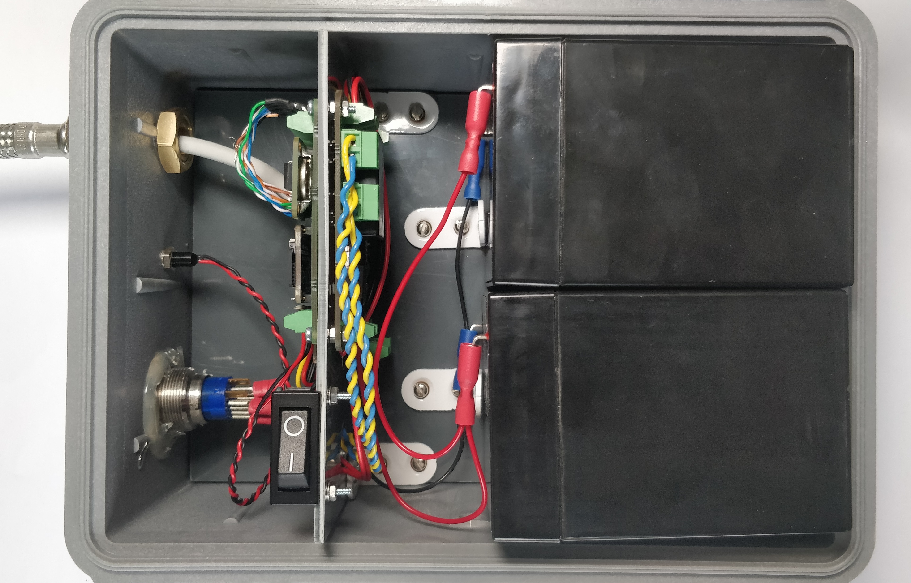
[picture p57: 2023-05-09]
docs/assets/images/Burrow_assembling/Final_assembling.jpg

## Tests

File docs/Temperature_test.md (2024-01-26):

# Temperature measurement

This page describes the tests realized with the embedded temperature sensor (RTD sensor based on a PT100).

## Measurement comparison

The temperature measurement of the system was compared with another temperature sensor in a controlled temperature test chamber. The two sensors were inserted into the test chamber, with a temperature setting from 25°C to 45°c with 2.5°c step :

<a href="../assets/images/User_description/Temp_measurement_Wacu_VS_Burrow_enclosure.jpg">
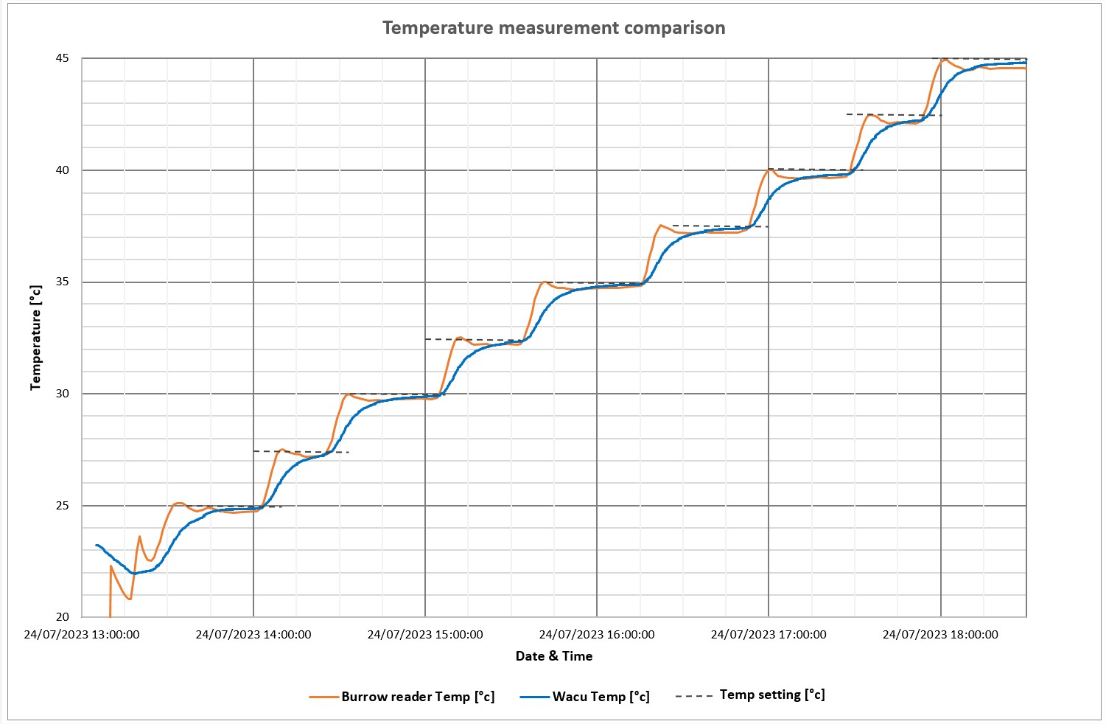
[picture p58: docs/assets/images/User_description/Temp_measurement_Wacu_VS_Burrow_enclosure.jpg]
Measurement report of the temperature between a WACU and a the RTD with a PT100

</a>

Results indicates that the gap between the two sensors is quite acceptable (~0.1°c). In addition the temperature difference between the two sensors and the settings can be explained by the temperature regulation of the test chamber, as the temperature overshoot.

Note : the inertia of the WACU logger can be explained by the specific mounting around the sensors during the test (plastic case)

Equipment used :

- Second temperature sensor : [MS5541-30](https://disensors.com/product/ms5541-30c-pressure-sensor/) (Sensor that equipped the WACU loggers of the MIBE)
- Test chamber : [DY60T](https://www.directindustry.com/prod/angelantoni-test-technologies/product-18270-1975819.html) humidity and temperature test chamber

## Temperature measurement inside the case

The temperature inside the burrow case was monitored during one month from the 20/06/2023 to the 19/07/2023.
Measurements indicates that the temperature inside the case does not exceed 53°C for a max outdoor temperature of 36.4°c, which is an acceptable temperature for the components.

<a href="../assets/images/User_description/Case_temp_measurement_outdoor.jpg">
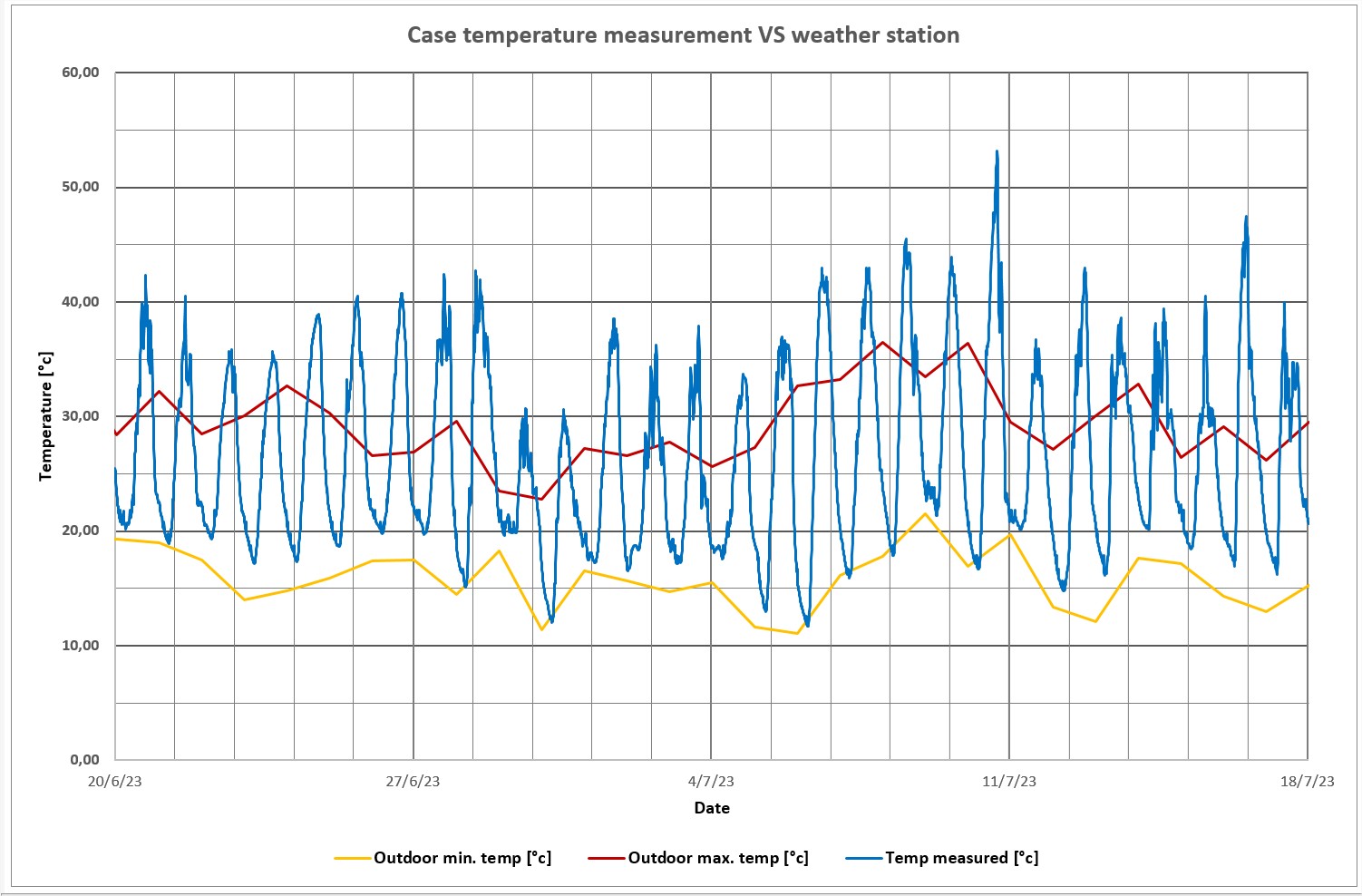
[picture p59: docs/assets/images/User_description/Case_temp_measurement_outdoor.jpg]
Measurement report of the temperature inside the case

</a>

The test was realized with i buttons sensors inside a silver colored [1150 hard case Pelicase](https://www.peli.com/eu/fr/product/cases/protector/1150) that is exposed to the sun.
The outdoor temperatures of the [site](https://maps.app.goo.gl/uQxYHY9fS9MLFkku9) comes from the [Entzheim weather station](https://www.infoclimat.fr/observations-meteo/temps-reel/strasbourg-entzheim/07190.html?graphiques).

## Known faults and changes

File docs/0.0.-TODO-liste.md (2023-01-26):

# TODO liste

## Electronique

### Main board 12V

#### modif à apporter

* Passer le projet sous KICAD
* Passer le maximum de composants en CMS et s'assurer de l'assemblage par le sous-traitant
* Noter sur le schéma le nom des pins des connecteurs (actuellement vide, seul est noté le nom du connecteur)

### Power board 5V

#### modif à apporter

* Passer le projet sous KICAD
* Passer le maximum de composants en CMS et s'assurer de l'assemblage par le sous-traitant
* Les capacités C2 100 nF et C3 100 nF sont à remplacer par des CMS du type 0805 105K X7R 50V SMD.
* Une piste de la carte power doit être coupée: celle qui connecte la tension batterie au power boost. Normalement un interrupteur d'arrêt doit permettre de couper l'alimentation entre batterie et le reste du système. Or cette piste fait une connexion permanente. [EDIT: Modif déjà apportée sur fritzing le 04/08/2022]
* La position des 4 trous est à changer. Deux sont trop proches du chargeur solaire (court circuit avec les vis), l'un trop proche du condensateur (court circuit) et l'autre trop proche du bornier à vis.

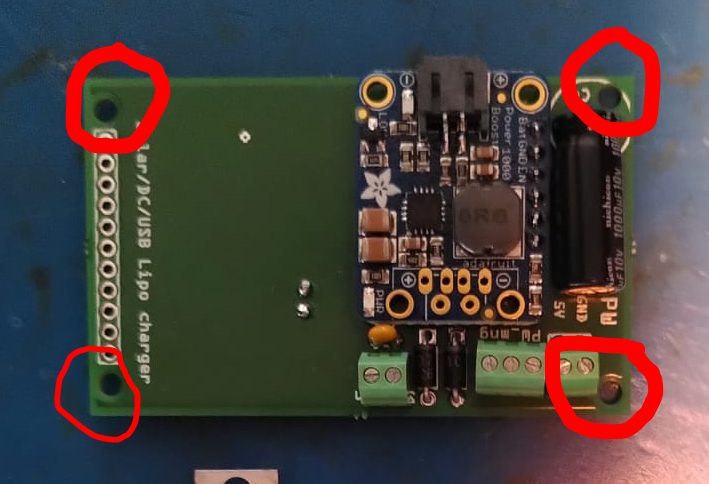
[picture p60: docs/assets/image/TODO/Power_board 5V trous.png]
Capture


#### Test à réaliser

* Mesures consommation des composants
* Test avec panneau solaire ( et amélioration de programmation associée)
* Protection contre la surchauffe: Avec l'aide d'un capteur de température, un arrêt logiciel de décharge de la batterie en cas de surchauffe a été programmé.  ( A VERIFIER, TESTER). Amélioration: envisager peut être une protection électronique interne et ne pas dépendre du bon fonctionnement du logiciel ?

### Power board 12V

#### modif à apporter

* Passer le projet sous KICAD
* Passer le maximum de composants en CMS et s'assurer de l'assemblage par le sous-traitant

### Système complet

* Test réel d'autonomie
  * Premier test réalisé avec une batterie 10Ah Li-Ion qui a permis au système d'antenne terrier de tourner pendant 5.6jours

## Informatique

Liste des choses à faire **indispensables** ou de l'ordre de l'amélioration.

* **Gestion du temps**
* **Gestion de la milliseconde**
J'ai ajouté une gestion de la ms. Elle n'est pas encore parfaite car par exemple les cas 40.914s , 40.230s, 40.734s, 41.238s peuvent se produire mais la différence de temps entre les événements est correcte. elle ne sert qu'à l'enregistrement pour l'instant, elle n'est pas implémentée dans le comptage des délais.

* **Le fichier de configuration** n'est pas bien lu et écrasé par la configuration en dur du code. Problème toujours présent lors de tests le 26 juillet 2022.

* **Ajout filtrage software lecture batterie** Suite à un premier test d'autonomie, le système s'est arrêté (seuil fixé en dessous de 3V), alors que la tension batterie mesuré au multimètre est de 3.16V. EDIT: FONCTIONNALITE AJOUTEE. A TESTER SUR LONG TEST D AUTONOMIE

* **Mode_day_only pas utilisable pour une activation de nuit** qui serait très pratique pour le suivi des hamsters. Modifier la condition

`if (hours_current < config.start_time or hours_current > config.stop_time)`

par une heure de démarrage et une durée (unixtime).

* **Lecture de la température** ne fonctionne plus/pas avec nouveau programme/nouvelle carte?

* mode Interruption plutôt qu'une lecture IR, pour connaitre sens passage

* Vérifier la taille de carte SD maximum supportée

## Mécanique

* **Version robuste à l'extérieure**
A vérifier l'étanchéité du flexible de conduit au niveau des raccords.

* **Bouton poussoir à changer** les BP momentanée (SW) et stable (PW) doivent être remplacés pour être compatibles avec des capuchons de protection étanches à la poussière ET à l'eau.

* **Maintien cartes élec dans valise**

## Test température au soleil

Test réalisé le 04 août 2022 sur « l'herbe » devant le bâtiment 24.

Thermomètre utilisé : thermomètre infrarouge sans-contact pouvant
mesurer de 0° à 100°C.

--------------------------------------------------------------------------
Valise      Valise      Valise      Sol au      Sol à
carton      blanche     noire       soleil      l'ombre
------------- ----------- ----------- ----------- ----------- -----------
  Avant          30          30          30
  installation
  13h25

  13h45          40          48          58          31          40

  14h45          **52°**     **52°**     **66°**     60          **33**

  15h45          51          51          65          57          35

16h45          48          50          66          60          35
--------------------------------------------------------------------------

La Pelicase sous le carton est noire.

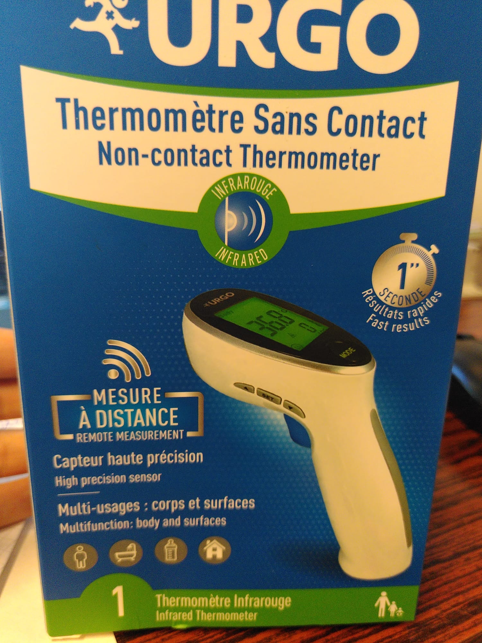
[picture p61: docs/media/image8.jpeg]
Thermomètre sans contact URGO


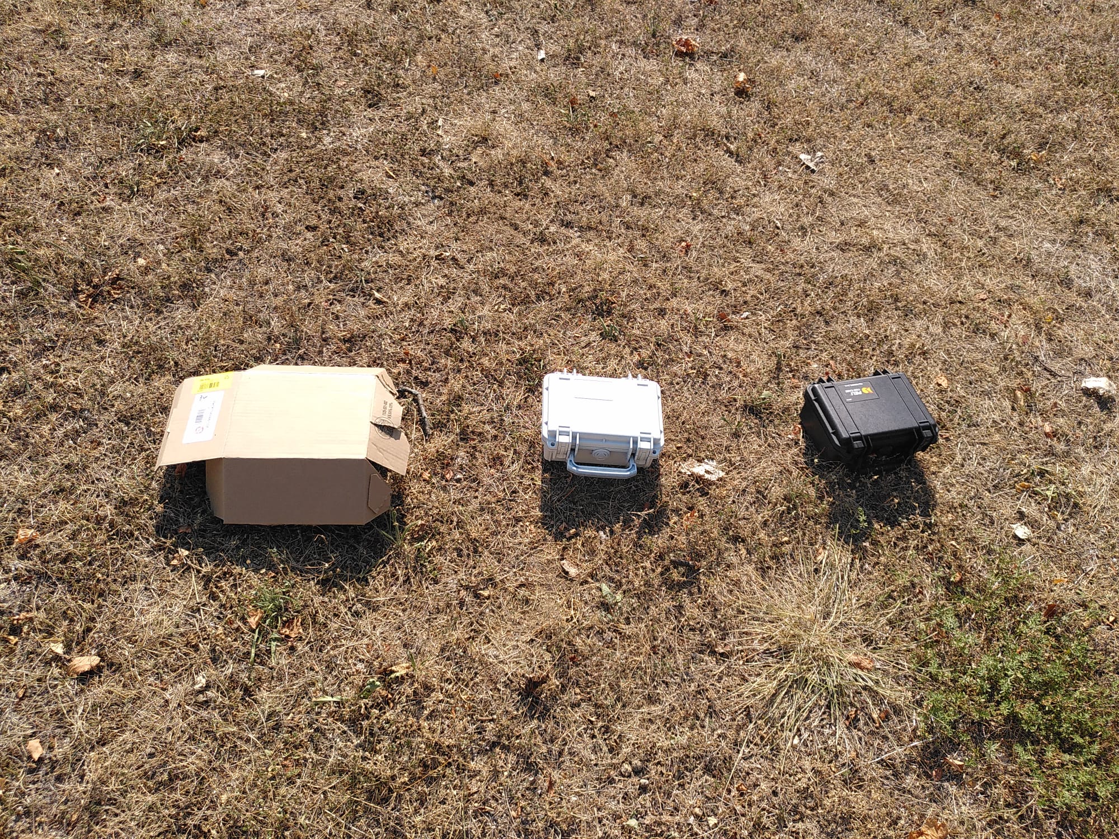
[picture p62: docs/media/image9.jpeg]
Valises de 3 couleurs différentes au soleil


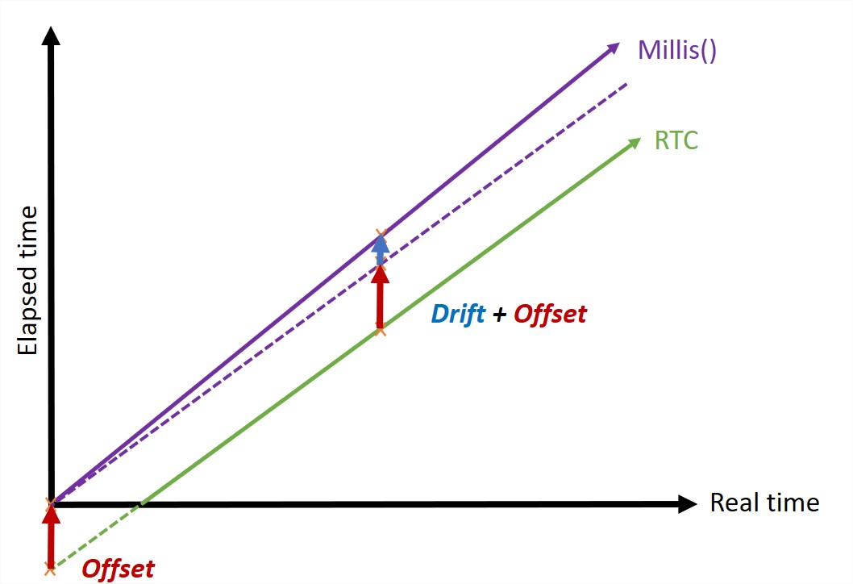
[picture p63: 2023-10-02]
docs/assets/images/User_description/Time_synchro_issue.jpg

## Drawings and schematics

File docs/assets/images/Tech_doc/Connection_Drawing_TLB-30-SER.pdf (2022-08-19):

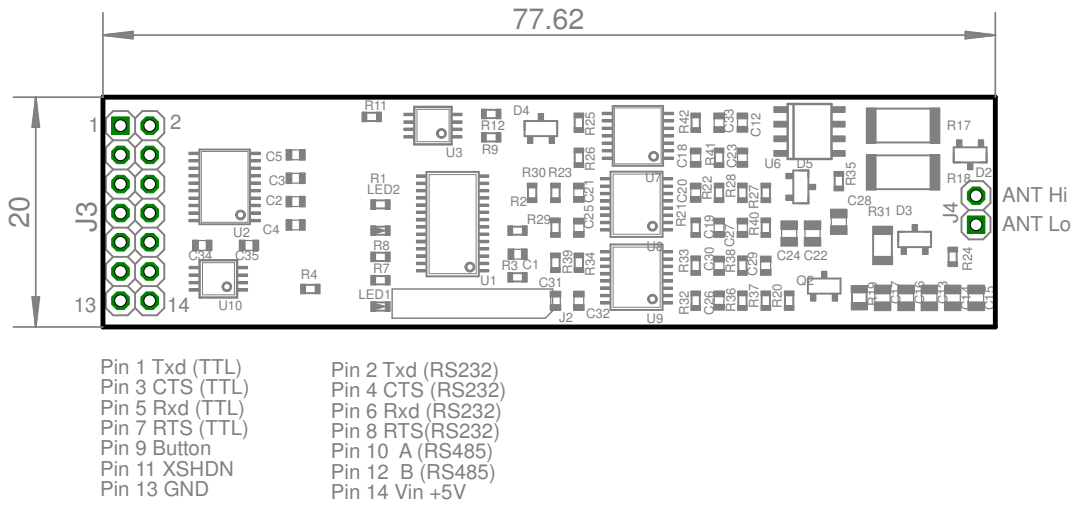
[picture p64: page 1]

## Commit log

2022-08-19 Create doc repository
    [Diagramme_de_Gantt_-_Projet_nichoir_à_oiseau_.xlsx]
2022-09-07 update index mkdocs help
    [Diagramme_de_Gantt_-_Projet_nichoir_à_oiseau_.xlsx]
2022-09-07 gitignore site subdirectories
    [Diagramme_de_Gantt_-_Projet_nichoir_à_oiseau_.xlsx]
2023-01-19 Mise à niveau vers mkdocs-materials
2023-01-26 code 404 fix
    [consumption.xlsx, current.xlsx]
2023-01-26 TODO for electronic boards
2023-02-14 creating page assembling antenna
2023-02-15 populate assembling instructions
2023-02-27 Update of RTC error code with flashing led
2023-03-08 Add project context and device description for user usage
2023-04-14 Update antenna assembling
2023-04-17 Add electronic assembly steps
2023-04-17 Add case assembly steps
2023-04-17 Update antenna assembly steps
2023-04-19 Add burrow case assembly description
    [Support_RFID.stl]
2023-04-19 Update Electronic boards + Pictures location
2023-04-19 Names change
    [Support_RFID.stl]
2023-04-19 Remove bill of material from instruction pages
2023-04-20 Folder organization + remove non-used pictures
    [Diagramme_de_Gantt_-_Projet_nichoir_à_oiseau_.xlsx, Support_RFID.stl]
2023-04-20 Add description for assembling
2023-04-21 Add BOM + Mods translation + Minor corrections
    [Bill of material.xlsx]
2023-04-24 Add estimation of possible records on SD memory card
    [Estimation of detection records on SD memory card.xlsx]
2023-04-26 Add autonomy estimation & Remove unused pictures
    [Bill of material.xlsx, Consumption_and_autonomy.xlsx, consumption.xlsx, current.xlsx]
2023-04-27 Add comments for calculation
    [Consumption_and_autonomy.xlsx]
2023-04-27 Update estimation of possible detection (memory) with new messages size (add uid, type and up)
    [Estimation of detection records on SD memory card.xlsx]
2023-04-27 Consumption correction for power boards
    [Consumption_and_autonomy.xlsx]
2023-05-02 Update consumption of RFID reader in search mode & autonomy
    [Consumption_and_autonomy.xlsx]
2023-05-04 Add message description + IR sensor positioning into the antenna
2023-05-11 Create assembly file description
2023-05-12 Add white background + Assembly file
2023-06-01 Update wire reference for antenna assembling
2023-06-01 Update calculation sheet to be more user-friendly
    [Consumption_and_autonomy.xlsx]
2023-06-05 Add pictures for schwegler antenna + update assembly instructions + minot corrections
    [Support_RFID.stl]
2023-06-07 Add instructions for nest box antenna assembling
2023-06-08 Add assembling instructions for nest box
2023-06-08 Update procedure and description with error indication (external led instead of internal) and battery check procedure
2023-06-08 Add nest box assembling overview
2023-06-09 Transfer manufacturing files to meca git + update links
    [Support_RFID.stl]
2023-06-09 Add screws indication for nest box assembling
2023-06-12 Add assembling pictures
2023-06-13 Update path for mechanical parts + Add new illustrations for assembling
2023-07-10 Add battery section
2023-07-11 Update instructions with new screw / nuts dimensions (following PCB modifications)
2023-07-11 Remove BOM from wiki docs and update link to elec git + link to BOM for boards without SMD
    [Bill of material.xlsx]
2023-07-11 Update schematic of electronic boards
2023-07-13 Update 12v battery to represent battery with MSDS provided
2023-07-18 Add battery documentation + correction of link to BOM
2023-07-21 Add clarification regarding the error code 4 (RTC battery error)
2023-07-24 Remove temperature shutdown description
2023-07-26 Add battery info + create temp test page
2023-07-27 Add temperature test description + minor correction
2023-09-20 Replace large nut by an existing reference of brass nut + picture update
2023-09-20 Update links of mechanical parts to master branch of meca repository + Add project description & pictures on the home page + battery reload instruction update
2023-09-20 Update indications about how to change the type of battery in the code & Add close_time parameter description
2023-09-20 Add max voltage admissible for solar panel
2023-09-21 Update assembling instructions with last version of nest box
2023-09-26 Add multiplex board description & instructions
2023-09-28 Correction of USB wiring instructions for nest box
2024-11-26 docs: Review antenna assembly for burrow device
    - Reviewed and clarified the assembly steps for the antenna in the burrow device.
    - Fixed markdown rendering issues on the antenna assembly instructions page.
    - Added local templates for CI (Continuous Integration) to improve the build process.
    - fix python version in pre-commit hook
